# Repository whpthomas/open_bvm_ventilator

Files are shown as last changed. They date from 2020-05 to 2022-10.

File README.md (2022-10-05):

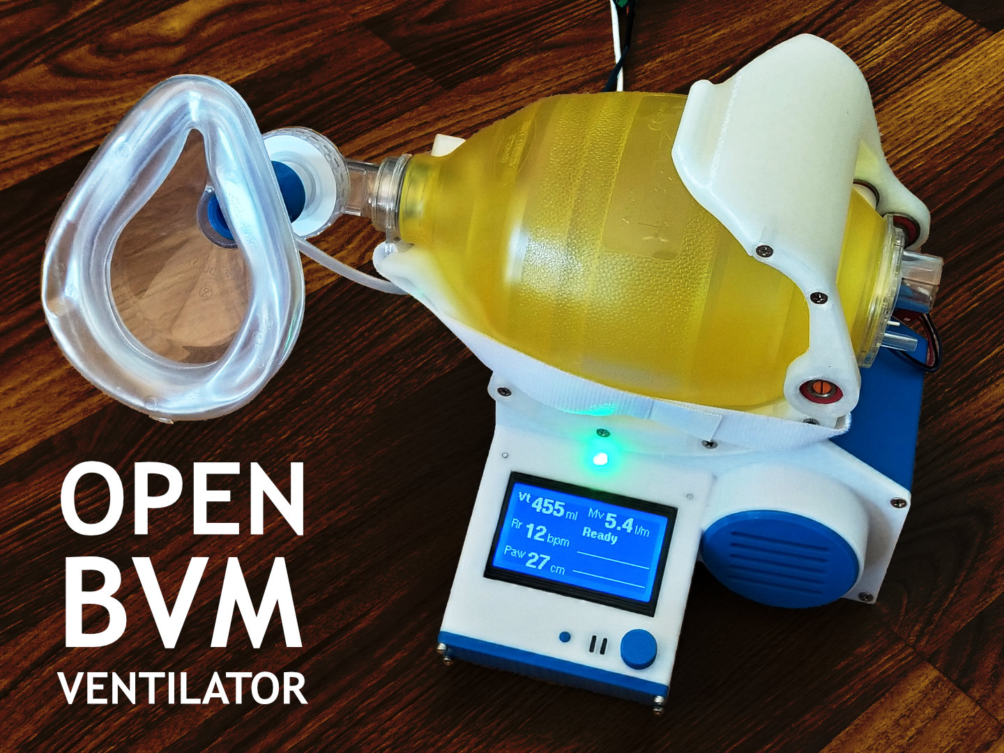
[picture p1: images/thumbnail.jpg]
Open BVM Ventilator


# Open BVM Ventilator project

This is a reference design and test platform for open source non-invasive bag valve mask ventilators. It features 3D printable parts and uses common off-the-shelf hardware and components.

3D Printable files can be found here and on [Thingiverse](https://www.thingiverse.com/thing:4335859).
Fusion 360 CAD files can be found here and on [GrabCAD](https://grabcad.com/library/open-bvm-ventilator-project-1).

## Specification

The Open BVM Ventilator is non-invasive and operates in universal mode (spontaneous pressure triggered ventilation with pressure-limited mandatory ventilation). It has been designed to meet all the applicable requirements outlined in the [Ventilator for COVID-19 use in Australia](spec/ventilator-covid-19-use-australia.pdf) document published on the [Australian Government, Department of Health, Therapeutic Goods Administration](https://www.tga.gov.au/ventilator-covid-19-use-australia) website.

### Assumptions

At the time this design was initiated it was assumed that early non-invasive ventilation with supplementary oxygen is beneficial for treating COVID-19 patients.

In order to meet all the requirements in the above document it is assumed that:

1. Supplementary oxygen will be provided to the bag via an externally regulated source (i.e. an oxygen cylinder or wall outlet).
2. A [HEPA exhalation filter](bom/BOM.md) will be installed between the manifold and mask.
3. A [PEEP regulator](bom/BOM.md) will be installed on the valve output to provide positive end-expiratory pressure.
4. An [extension hose](bom/BOM.md) may be used to connect the mask to the patient. However if used, the extension hose should be connected between the bag and the valve to limit the amount of dead space in the gas exchange.
5. The mask will be strapped to patient in order to provide a hands free airtight seal.

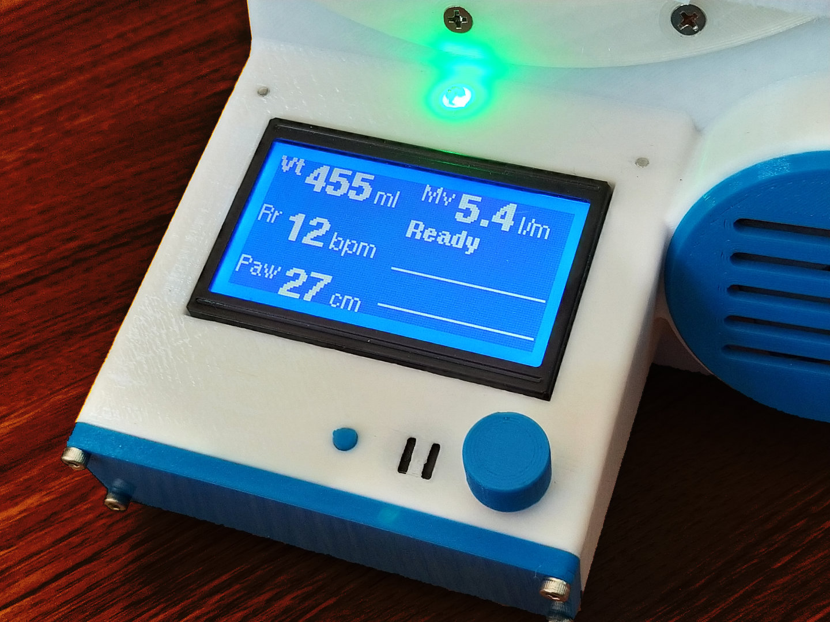
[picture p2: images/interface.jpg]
Open BVM Ventilator Interface


### Capabilities

The current Open BVM Ventilator design has the following capabilities:

* Respiratory air and oxygen is fed through a bag valve mask (Ambu bag) which is an approved medical device for hand resuscitation. The pressure sensor manifold is 3D printed with food grade PLA.
* All controls are adjustable in real time and provide live feedback though mechanical output and the user interface.
* Minute Volume (Mv) and Peak Inspiratory Pressure (Pip) are displayed after each respiratory cycle.
* Pressure-limited mandatory ventilation is controlled via the Respiratory Rate (Rr) and Tidal Volume (Vt).
* Spontaneous ventilation is triggered via negative pressure on the the pressure sensor attached to the manifold (Controls page / Trigger Pressure). 
* Positive end expiratory pressure (PEEP) is provided by a [regulator](bom/BOM.md) attached to the valve output.
* Quick adjustment of Tidal Volume (Vt), Respiratory Rate (Rr) and Plateau Airway Pressure (Paw) is available on the user interface main page.
* Airway pressure safety is set via the maximum pressure limit (Limits page / Pressure / Maximum).
* Pressurised air is not required, therefore the unit can be operated outside of an ICU using only bottled oxygen and a power supply.
* All ventilator controls are accessed via the LCD display, stop button and encoder on the [Reprap Discount Full Graphic Smart Controller](https://reprap.org/wiki/RepRapDiscount_Full_Graphic_Smart_Controller).
* Tidal Volume has been [calibrated and verified](spec/calibration.pdf).
* Both visual and audible alarms are generated and logged on the Events page.
* 12v power can be provided via an AC adapter or external battery.
* All parts can be 3D printed with food safe PLA plastic.

These capabilities have been verified with static tests using a manometer but will require more comprehensive dynamic testing to be considered validated. Some dynamic testing using a water column to simulate pressure and volume has also been undertaken.

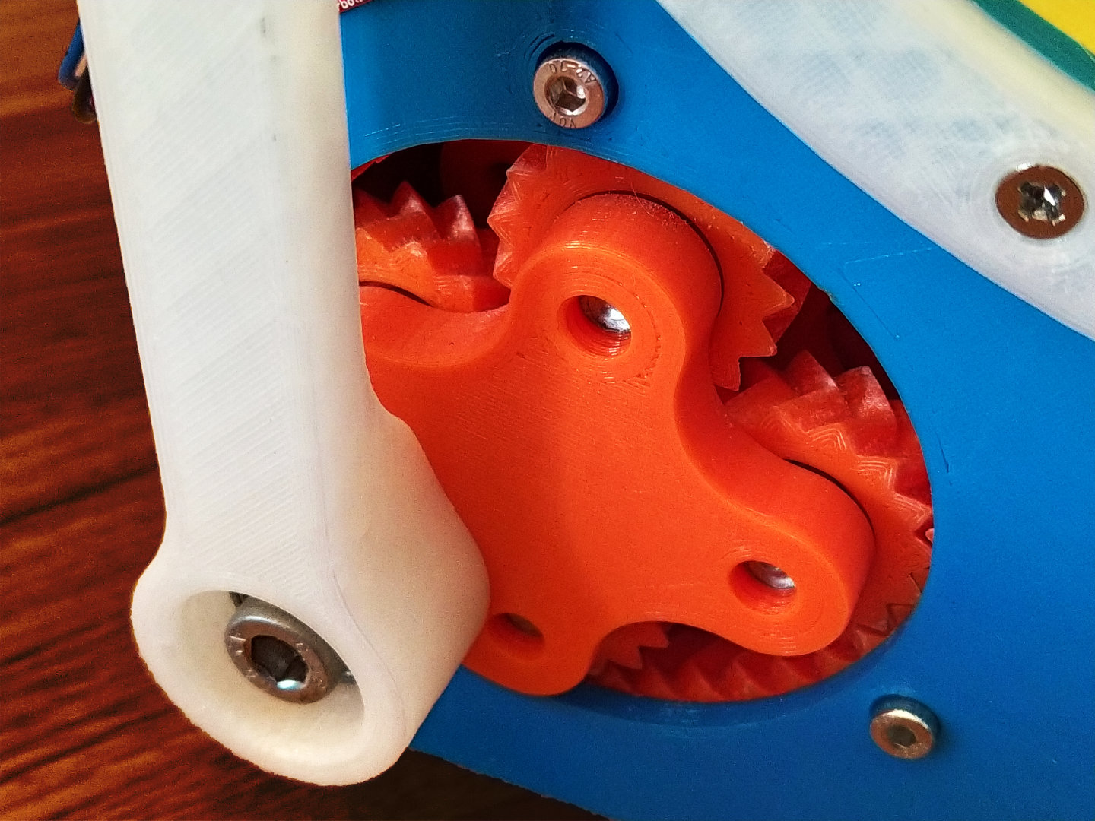
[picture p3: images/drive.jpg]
Open BVM Ventilator Drive


### Outstanding Issues

1. Maximum inspiratory and expiratory flow is limited to 35 l/min by the maximum stepper motor RPM and torque. I will attempt to resolve this by using a TMC2209 driver and by adding a DC Step Up to 24v for the Stepper motor power supply.
2. The current stepper driver is noisy and will to be replaced with a TMC2209 driver. However this will require the addition of a cooling fan.
3. **Time and resources:** when I started this project a critical lack of ventilators was in the news. Now that we have *flattened the curve* - particularly here in Australia - not so much. I self-funded this project and spent weeks working on it. I need to get back to work and earn a living, so unless others want to pitch in and help, I am not sure how much more I can do on my own.

## Hardware

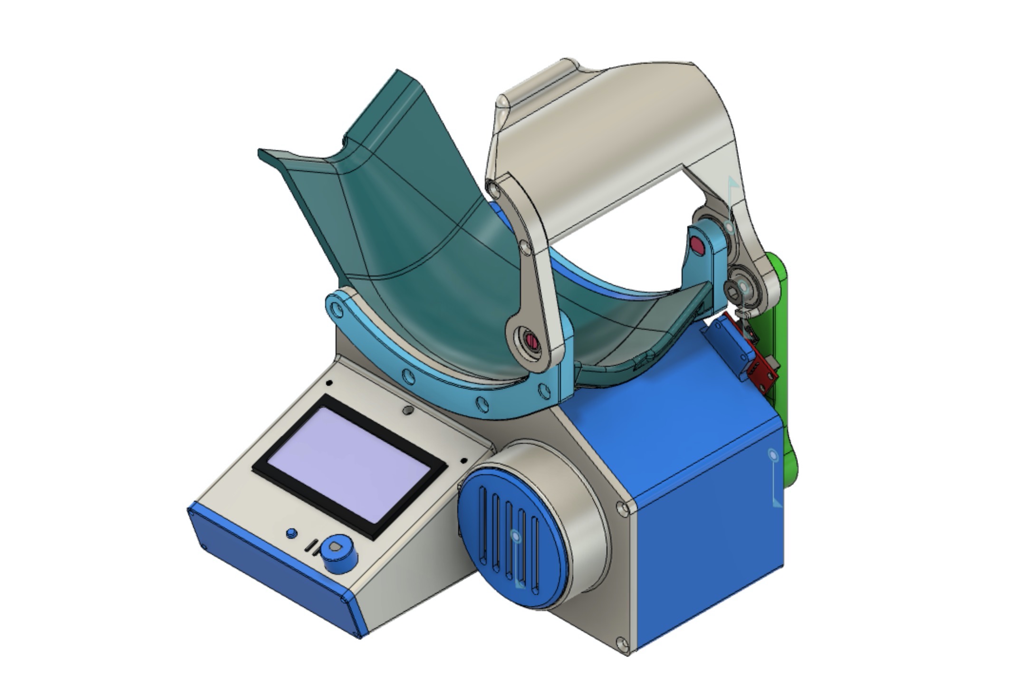
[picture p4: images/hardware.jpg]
Open BVM Ventilator Hardware


The Open BVM Ventilator is comprised of 25 x 3D printed parts and various off-the-shelf hardware, electronic components and fasteners.

A list of all the required hardware, fasteners, electronic components and 3D printed parts can be found in the **[Bill of Materials](bom/BOM.md)**.

## Firmware

The firmware features a real time model view controller architecture with custom stepper speed control that supports linear acceleration with rpm adjustment inside position changes.

The firmware can be downloaded, compiled and uploaded to the Arduino Uno board using the [Arduino IDE](https://www.arduino.cc/). 

The firmware is dependent on the following libraries:

* [BME280I2C](https://github.com/finitespace/BME280)
* [FastIO](https://github.com/whpthomas/FastIO)
* [U8g2lib](https://github.com/olikraus/u8g2)

The factory reset function found on the System Page should be selected the first time the system is run to set all the EEPROM control variables to know values.

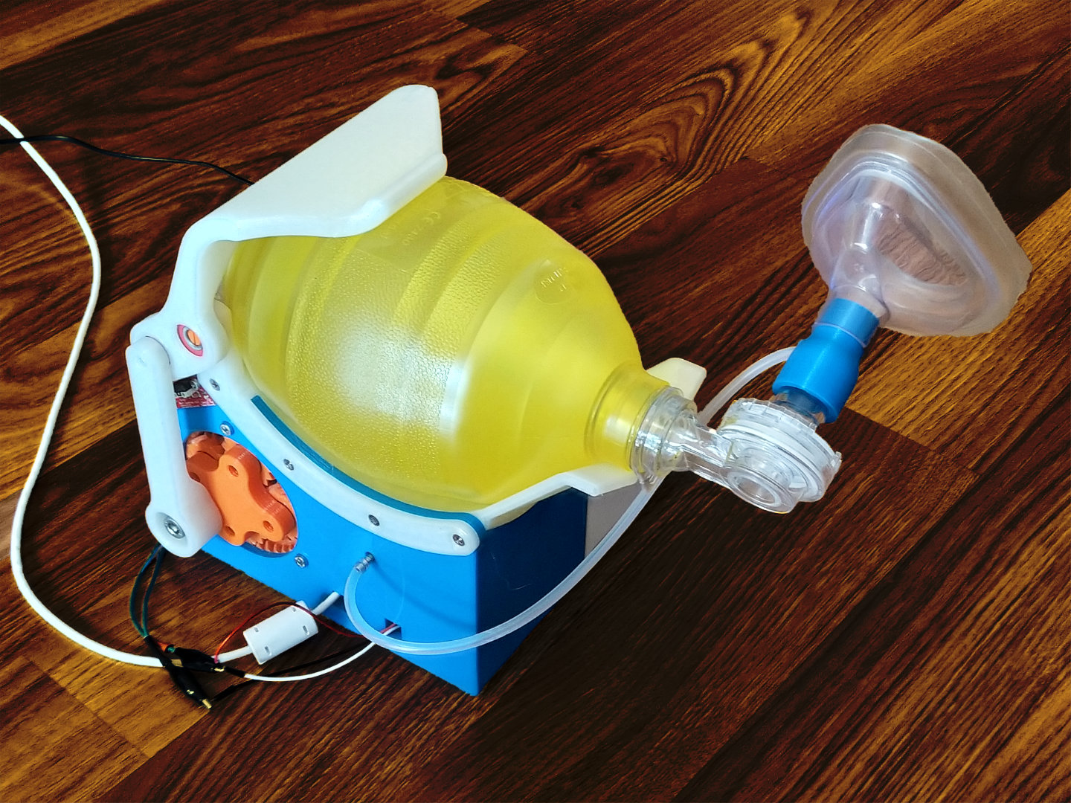
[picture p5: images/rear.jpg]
Open BVM Ventilator Rear


## Electronics

A control shield for the Arduino Uno can be found at [easyeda.com/whpthomas/open-bvm-ventilator-shield](https://easyeda.com/whpthomas/open-bvm-ventilator-shield). The shield has been designed to allow all the electronic components to be easily connected using either Dupont connectors or by directly soldered wires. The circuit supports use of either the TB6560 or A4988 (or compatible) stepstick driver.

Fully assembled boards can be ordered directly from [JLCPCB](https://jlcpcb.com/), [PCBWay](https://www.pcbway.com/) or other suitable PCB prototyping services using the Gerber files, bill of materials and pick and place files found in the [`/pcb`](https://github.com/whpthomas/open_bvm_ventilator/tree/master/pcb) folder.

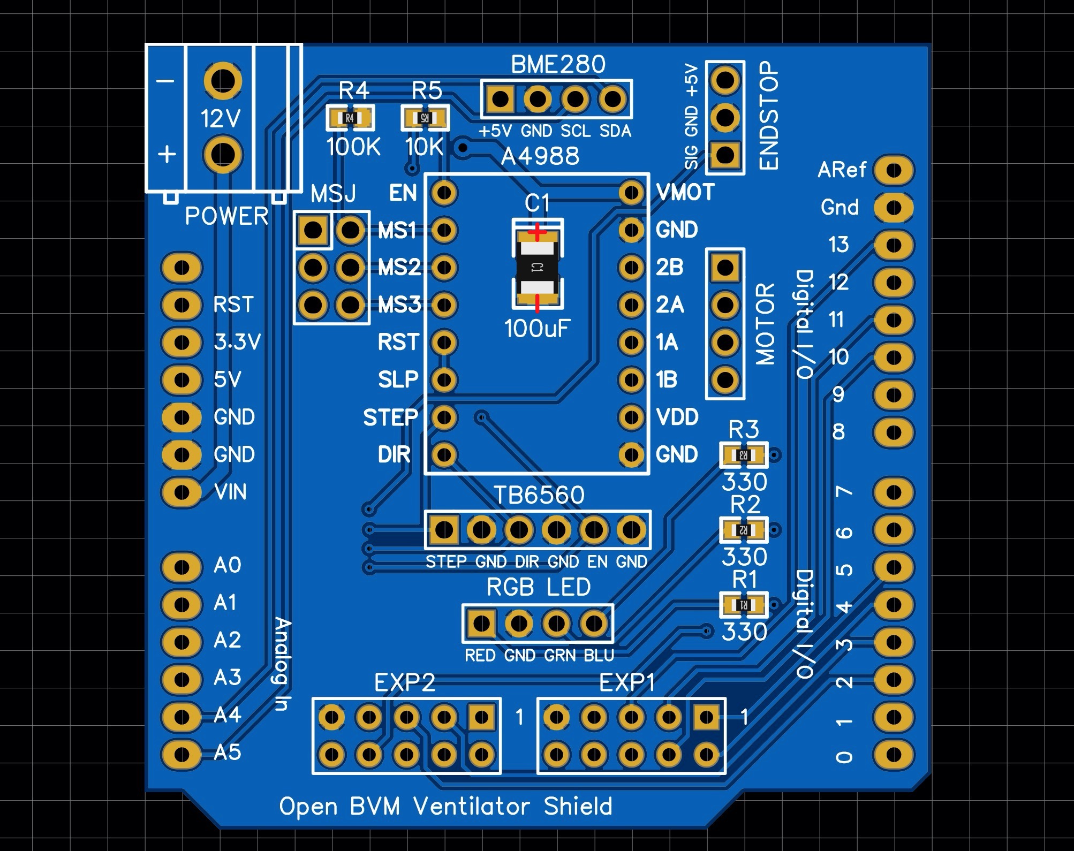
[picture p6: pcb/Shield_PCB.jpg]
Arduino Uno Shield


The following digital pins on the Arduino Uno are used in the [schematic](https://github.com/whpthomas/open_bvm_ventilator/blob/master/pcb/Shield_SCH-v1.pdf):

* **2** Controller Rotary Encoder A (Interrupt 0)
* **3** Controller Rotary Encoder B (Interrupt 1)
* **4** Controller Rotary Encoder Button
* **5** Controller Buzzer
* **6** Controller Stop Button
* **7** LED Red
* **8** LED Green
* **9** LED Blue
* **10** LCD Chip Select (SS)
* **11** LCD Data In (MOSI)
* **13** LCD Clock (SCK)
* **A0** Home Endstop
* **A1** Stepper Driver Step
* **A2** Stepper Driver Direction
* **A3** Stepper Driver Enable
* **A4** BME280 Pressure Sensor IC2 SDA
* **A5** BME280 Pressure Sensor IC2 SCK

#### A4988 Jumper Settings

Jumpers are used on the MSJ header to set the microstep resolution. The default configuration is to place a jumper across MS1 and MS2 for 1/8 microstep resolution.

MS1|MS2|MS3|Microstep Resolution
----|----|----|----
Low|Low|Low|Full step
High|Low|Low|1/2 step
Low|High|Low|1/4 step
High|High|Low|1/8 step
High|High|High|1/16 step

#### TB6560 Switch Configuration

Switches are used on the TB6560 stepper driver to set the current and microstep resolution.

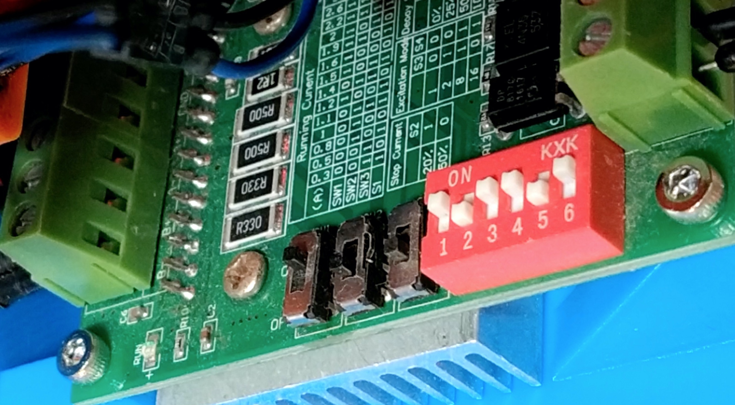
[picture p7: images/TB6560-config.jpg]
TB6560 Configuration


I recommend configuring the TB6560 with the following settings.

Switch|State|Configuration
----|----|----
SW1|ON|1.2A
SW2|OFF|1.2A
SW3|OFF|1.2A
S1|ON|1.2A
S2|OFF|50% Stop Current
S3|ON|1/8 steps
S4|ON|1/8 steps
S5|OFF|50% Delay
S6|ON|50% Delay

----

# TERMS OF USE

Open BVM Ventilator reference designs are intended for educational purposes, ARE NOT CERTIFIED FOR MEDICAL USE, ARE PROVIDED "AS IS" AND "WITH ALL FAULTS". Dr. Henry Thomas DISCLAIMS ALL OTHER WARRANTIES, EXPRESS OR IMPLIED, INCLUDING BUT NOT LIMITED TO, ANY IMPLIED WARRANTIES OF MERCHANTABILITY OR FITNESS FOR A PARTICULAR PURPOSE. Dr. Henry Thomas may make changes to reference design specifications and descriptions at any time, without notice.

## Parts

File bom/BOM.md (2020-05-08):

# Bill of Materials

This is the bill of materials for the [Open BVM Ventilator](https://github.com/whpthomas/open_bvm_ventilator) project. Where possible I have chosen widely available common off-the-shelf (COTS) components. However the machine screws I used are metric which may be harder to source in North America.

## Medical Supplies

Part|Description|Quantity
----|----|----
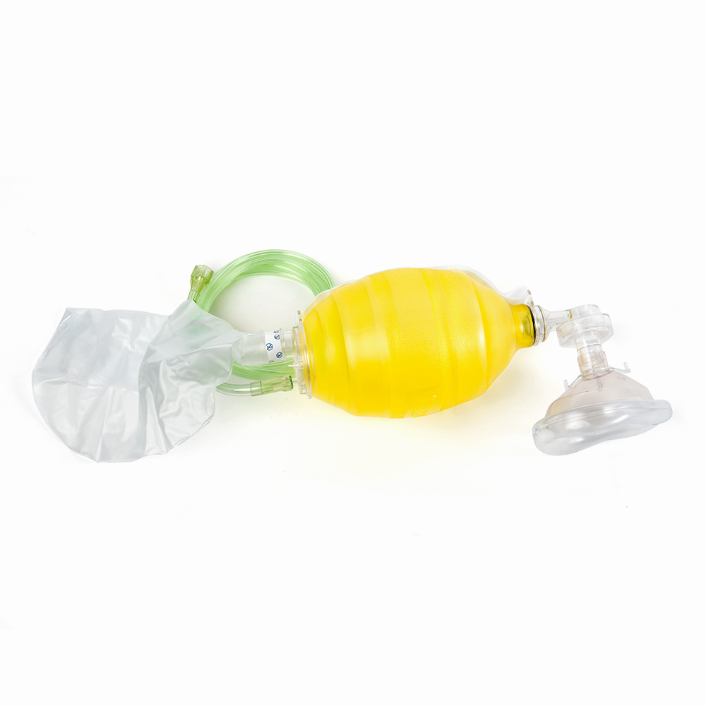
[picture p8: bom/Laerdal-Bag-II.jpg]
Laerdal Bag II
|[Laerdal Bag II](https://www.laerdal.com/au/item/845111), [LSR](https://www.laerdal.com/au/item/87005133), or equivalent adult sized bag valve mask hand  resuscitator (e.g. Ambu Bag).|1
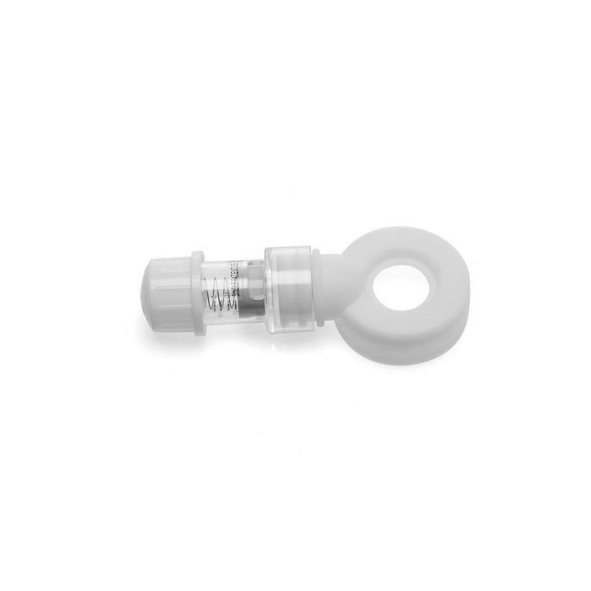
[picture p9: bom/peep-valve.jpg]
PEEP Valve
|[PEEP Valve](https://www.laerdal.com/au/item/845240) (5-20 cm H2O).|1
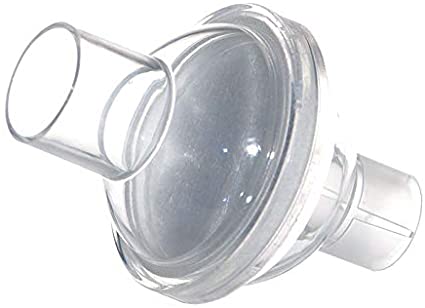
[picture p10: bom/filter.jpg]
HEPA Filter
|HEPA Filter.|1
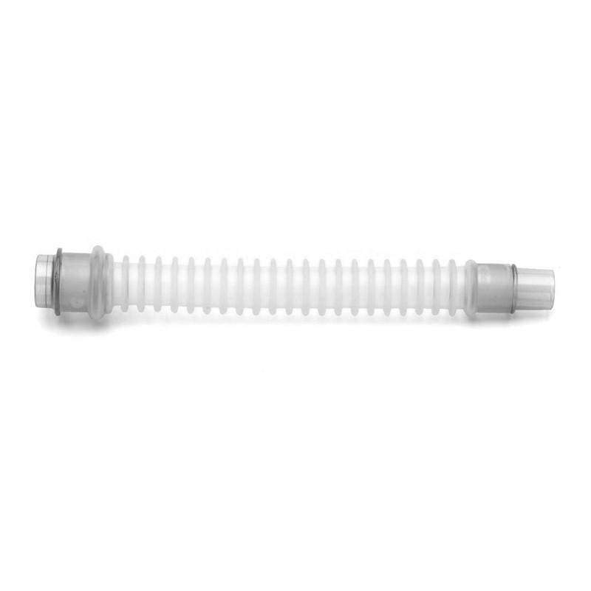
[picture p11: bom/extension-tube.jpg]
Extension Tube
|[Silicone Extension Tube](https://www.laerdal.com/au/item/871000).|1
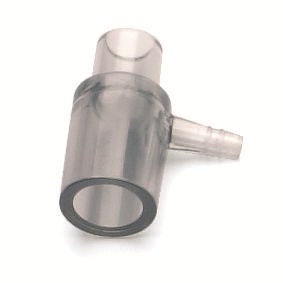
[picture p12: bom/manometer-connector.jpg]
Manometer Connector
|[Manometer connector](https://www.laerdal.com/au/item/850900). This barb requires a 6mm oxygen hose.|Option

## Hardware

Part|Description|Quantity
----|----|----
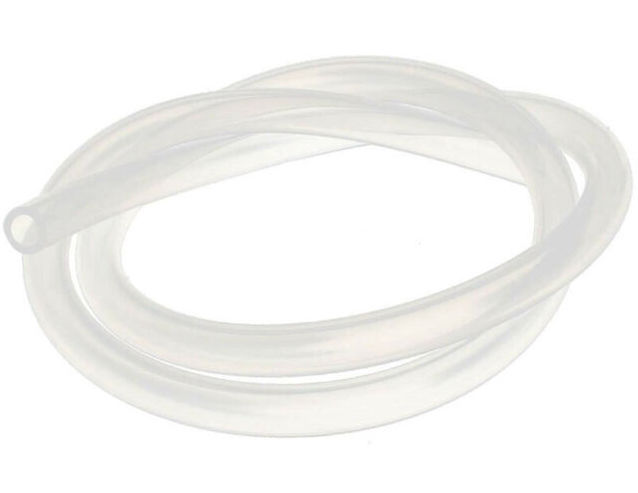
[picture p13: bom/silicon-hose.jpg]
Silicon Hose
|5mm OD x 3mm ID x 250mm L food grade silicon hose.|1
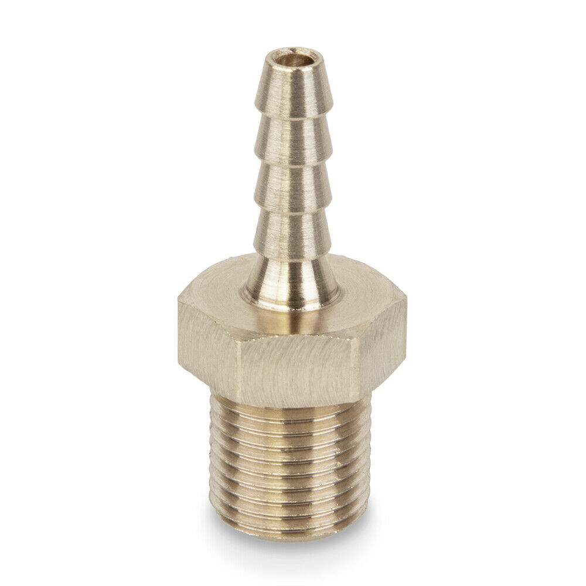
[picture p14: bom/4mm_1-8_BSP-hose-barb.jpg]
Hose Fitting
|1/8" BSP to 4mm barb hose fitting. This barb protrudes from the back of the housing base and is used to connect the manifold hose to the pressure sensor. If you decide to use the optional [manometer connector](https://www.laerdal.com/au/item/850900) a 1/8" BSP to **6mm** barb hose fitting should be used.|1
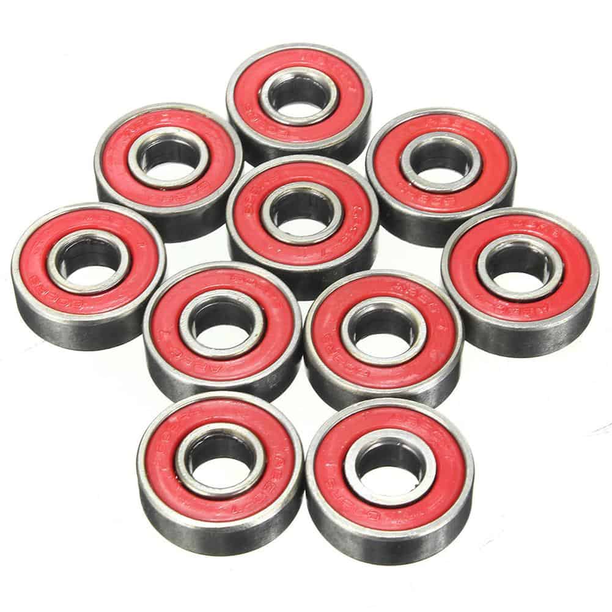
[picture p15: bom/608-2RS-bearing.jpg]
Bearing
|608-2RS 22mm OD x 8mm ID x 7mm W skate bearings.|11
M3x6mm Machine Screws|M3 x 6mm stainless socket head cap screws are used to attach the stepper motor to the ring mount, and the Arduino Uno, stepper driver and endstop circuit boards to the base.|13
M3x12mm Machine Screws|M3 x 12mm stainless socket head cap screws are used to attach the interface front cover to the interface panel.|4
M3x16mm Machine Screws|M3 x 16mm stainless socket head cap screws are used to attach the [Reprap Discount Full Graphic Smart Controller](https://reprap.org/wiki/RepRapDiscount_Full_Graphic_Smart_Controller) to the interface panel.|2
M4x12mm Countersink Screws|M4 x 12mm stainless countersink screws are used to assemble the cradle, hinges and main housing.|13
M4x16mm Machine Screws|M4 x 16mm stainless socket head cap screws are used to assemble the planetary gear module and attache it to the housing.|12
M8x16mm Machine Screws|M8 x 16mm stainless socket head cap screws are used to attach bearings to the planet intermediate carrier to gang 1, bearings the planetary output carrier to gang 2 and bearings to the tie rod between the planetary output and press arm.|10

## Electronic components

Part|Description|Quantity
----|----|----
Arduino Uno|Arduino Uno Rev 3|1
BME280 Sensor Module|BME280 humidity, barometric pressure and temperature sensor module with 3 wire I2C interface.|1
Makerbot endstop|Makerbot 3D printer endstop.|1
Stepper Motor|NEMA17 2 phase stepper motor with 1.8 degree step angle, 60mm motor length, and 1.5A current rating.|1
Power Supply|12 volt 1 amp AC-DC power supply with 5.5mm OD 2.5mm ID center-positive DC plug.|1
RGB LED|Common cathode 5mm RGB LED.|1
Arduino Uno|[Reprap Discount Full Graphic Smart Controller](https://reprap.org/wiki/RepRapDiscount_Full_Graphic_Smart_Controller). This component is a widely available LCD interface controller commonly used on many 3D printers.|1
Stepper Driver| TB6560 stepper driver.|1
Jumper Wires|Bread board jumper wires|20 leads

## 3D printed parts

These parts can be printed in PLA or PETG on a 200mm W x 150mm D x 150mm H bed.

Part|Description|Quantity
----|----|----
Base|`base.stl` This part comprises the main body of the ventilator housing. The circuit boards and planetary drive are mounted inside this enclosure.|1
Bearing Pin|`bearing_pin.stl`These press fitted parts connect the the 608 bearings in the press arm assembly to the left an right hinge plates.|2
Control Knob|`control_knob.stl` This part is press fitted onto the encoder of the [Reprap Discount Full Graphic Smart Controller](https://reprap.org/wiki/RepRapDiscount_Full_Graphic_Smart_Controller)|1
Cradle|`cradle.stl` This part links the housing base and interface panel with the left and right hinge plates.|1
Hex Link|`hex_link.stl` This part connects the Planet Intermediate carrier with the Planetary Gear module 2.|1
Hinge Plate Right|`hinge_plate_l.stl` This part connects the press arm assembly to the the cradle and housing.|1
Hinge Plate Left|`hinge_plate_r.stl` This part connects the press arm assembly to the the cradle and housing.|1
Interface Front Cover|`interface_front_cover.stl` This part attaches to the front interface panel and holds the [Reprap Discount Full Graphic Smart Controller](https://reprap.org/wiki/RepRapDiscount_Full_Graphic_Smart_Controller) in place.|1
Interface Panel|`interface-panel.stl` This part is attached to the front of the base housing.|1
Mask Manifold|`mask_manifold.stl` This part attaches between the mask and valve and connects the opposite end of the 5mm silicon hose with the pressure sensor.|1
Motor Cover|`motor_cover.stl` This part snaps onto the interface panel and covers the rear of the stepper motor.|1
Planet Intermediate|`planet_intermediate.stl` This carrier holds the planetary gang 1 bearings in place and drives gang 2 via the hex link.|1
Planet Output|`planet_output.stl` This carrier holds the planetary gang 2 bearings in place and drives the tie rod.|1
Planetary Gear Module Gang 1|`planetary_gang_1_x-x.stl` This part is the gang 1 print-in-place planetary gear module. There are two versions of this file, one for a steeper motor with a 3.9mm keyway and the other for a 4.5mm keyway.|1
Planetary Gear Module Gang 2|`planetary_gang_2.stl` This part is the gang 2 print-in-place planetary gear module which is driven via the hex link by the intermediate carrier.|1
Press Bracket|`press_bracket.stl` This bracket is attached to opposite side of the press arm.|1
Press Arm|`press-arm.stl` This part is attached via bearings and pins to the hinge plates.|1
Pressure Sensor Base|`pressure_sensor_base.stl` This part encloses the BME280 sensor, that should be sealed with Sikaflex 227 (or equivalent).|1
Pressure Sensor Mount|`pressure_sensor_mount.stl` This part connects the BME280 sensor to the 4mm hose barb and is attached to the base with cyanoacrylate gel glue.|1
Ring Mount|`ring_mount.stl` This part connects the planetary gear module to the stepper motor.|1
Ring Spacer|`ring_spacer.stl` This part connects the planetary gear gang 1 & 2 together.|1
Spacer|`spacer.stl` This part separates the tie rod bearing from the planetary output carrier.|1
Stop Button|`stop-button.stl` This part links the tactile switch on the [Reprap Discount Full Graphic Smart Controller](https://reprap.org/wiki/RepRapDiscount_Full_Graphic_Smart_Controller) with the interface panel.|1
Tie Rod|`3dp-tie-rod.stl` This part links the planetary output carrier with the press arm.|1

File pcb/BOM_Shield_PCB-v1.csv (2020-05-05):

ID | Name | Designator | Footprint | Quantity | Manufacturer Part | Manufacturer | Supplier | Supplier Part | LCSC Assembly
1 | 100K | R4 | R0603 | 1 | 0603WAF1003T5E | UniOhm | LCSC | C25803 | Yes
2 | 10K | R5 | R0603 | 1 | 0603WAF1002T5E | UniOhm | LCSC | C25804 | Yes
3 | 100uF | C1 | CAP-SMD_L7.3-W4.3-R-RD | 1 | TAJE107M025RNJ | AVX | LCSC | C7230 | Yes
4 | 330 | R3,R1,R2 | R0603 | 3 | 0603WAF3300T5E | UniOhm | LCSC | C23138 | Yes

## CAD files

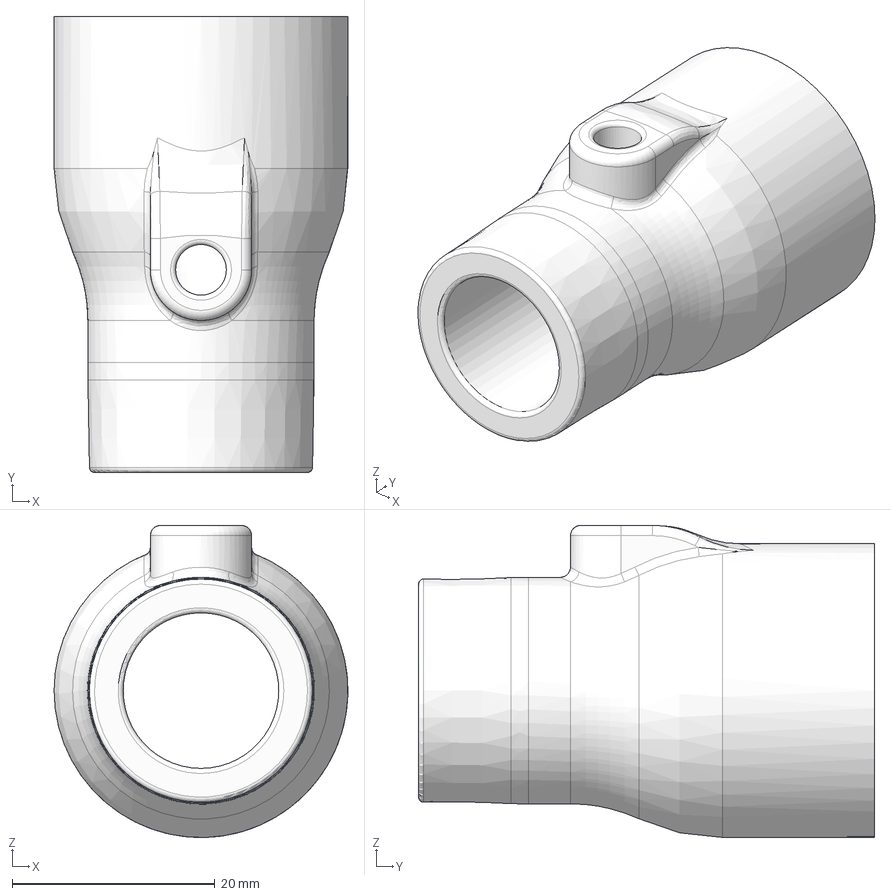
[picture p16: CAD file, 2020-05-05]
cad/Mask Manifold v5.step
29.0 x 45.0 x 30.8 mm

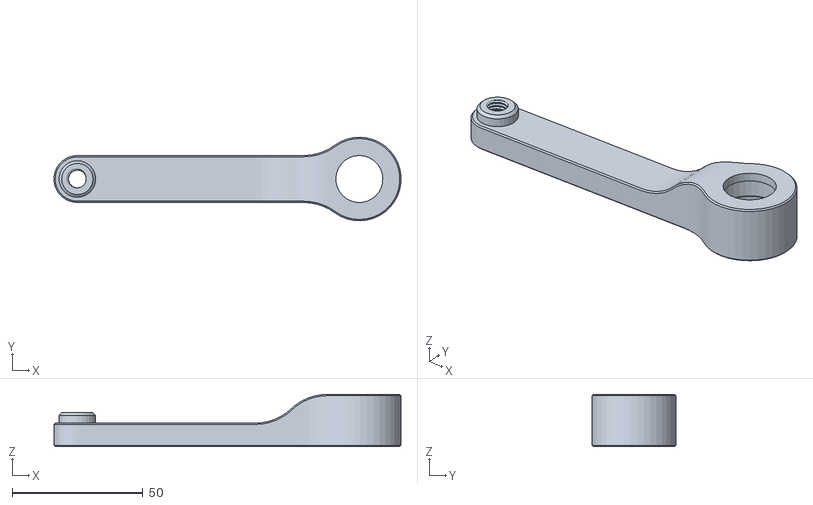
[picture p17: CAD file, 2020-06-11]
stl/tie_rod.stl
132.9 x 32.0 x 20.0

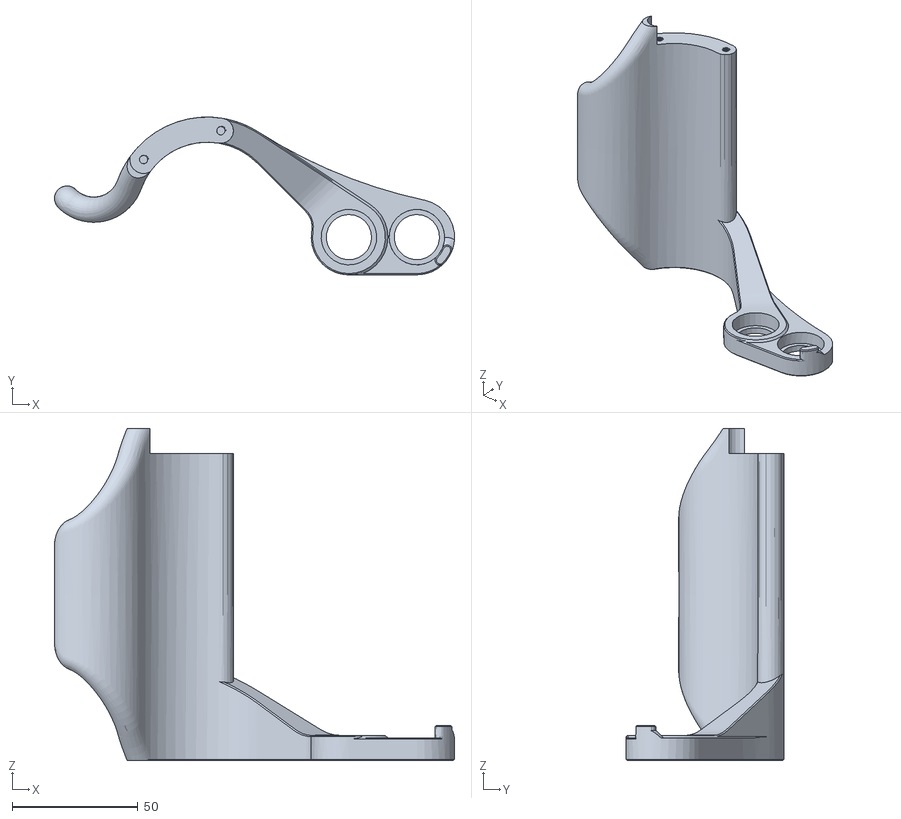
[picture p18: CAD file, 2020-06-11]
stl/press_arm.stl
159.0 x 62.7 x 132.0

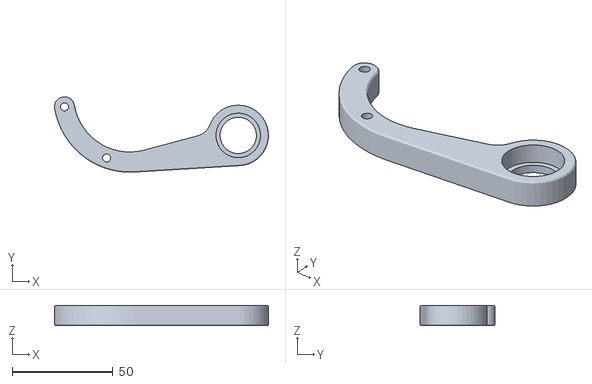
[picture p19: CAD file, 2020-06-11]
stl/press_bracket.stl
106.1 x 37.3 x 10.0

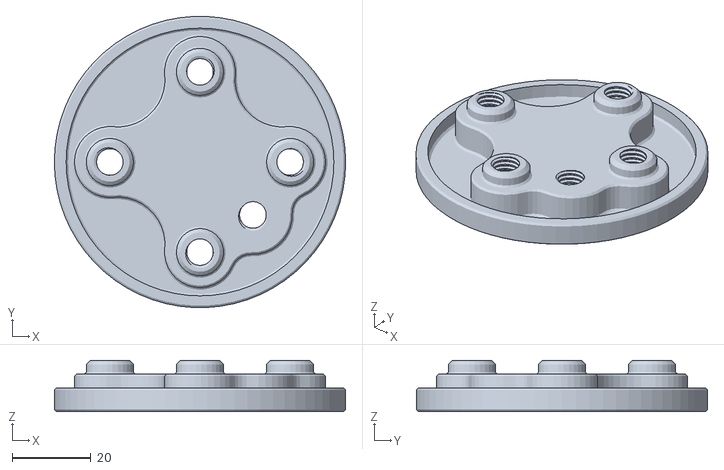
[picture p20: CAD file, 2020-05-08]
stl/planet_output.stl
74.0 x 73.9 x 13.0

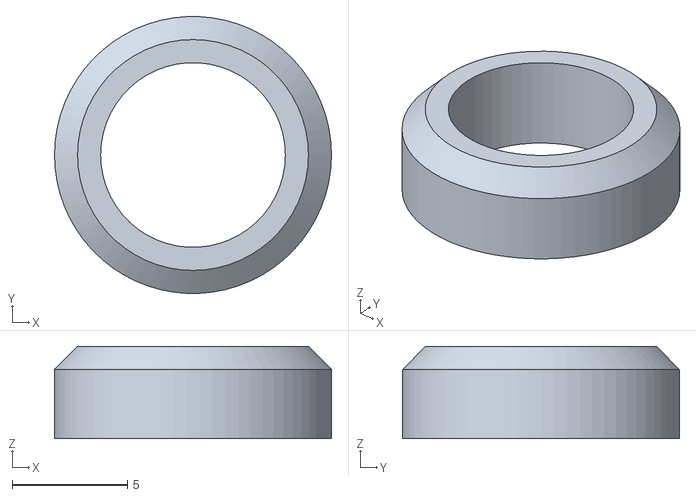
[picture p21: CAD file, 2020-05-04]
stl/spacer.stl
12.0 x 12.0 x 4.00

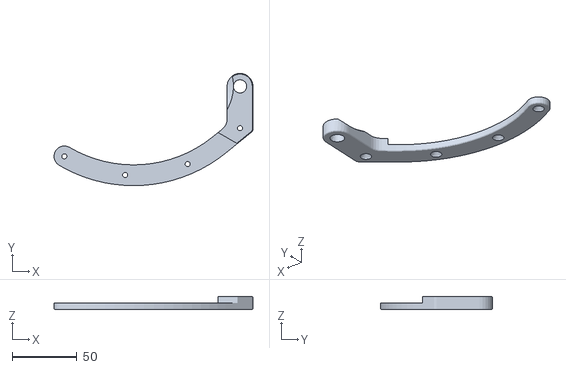
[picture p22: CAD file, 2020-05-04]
stl/hinge_plate_l.stl
153.5 x 86.6 x 10.00

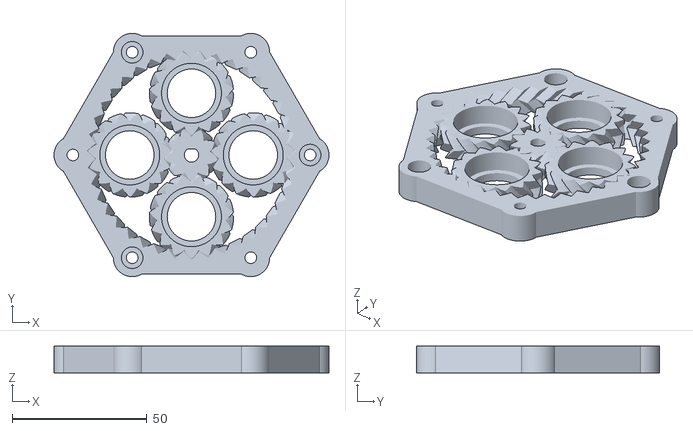
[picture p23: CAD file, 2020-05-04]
stl/planetary_gang_1_4-5.stl
102.0 x 90.2 x 10.0

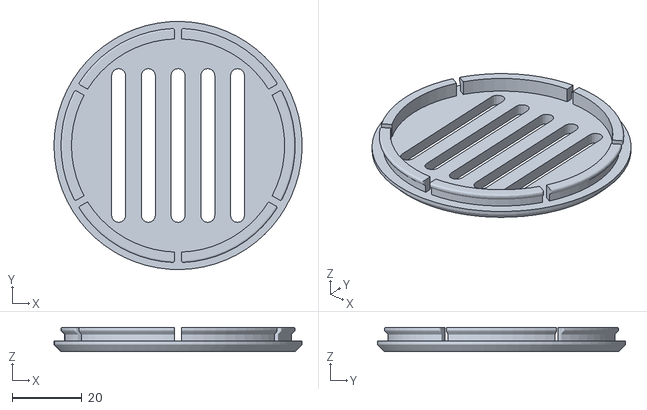
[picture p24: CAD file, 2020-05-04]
stl/motor_cover.stl
71.0 x 71.0 x 7.00

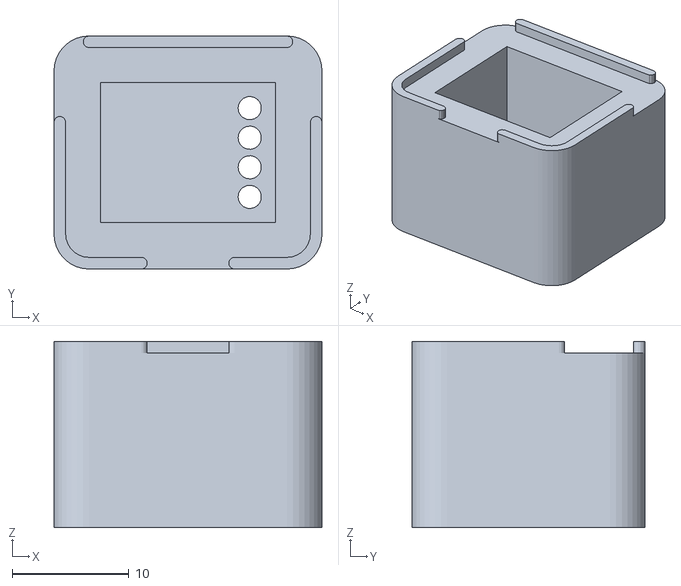
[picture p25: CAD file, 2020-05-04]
stl/pressure_sensor_base.stl
23.0 x 20.0 x 16.0

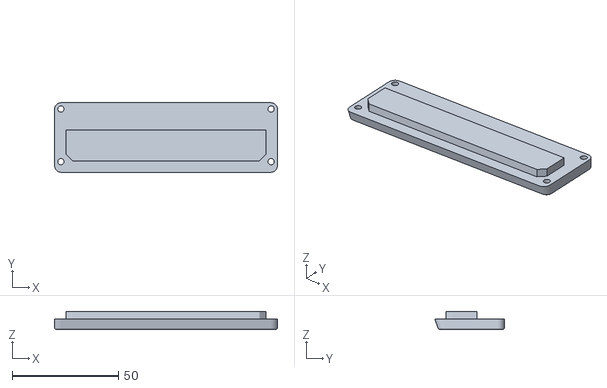
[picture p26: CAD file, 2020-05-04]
stl/interface_front_cover.stl
105.0 x 32.8 x 8.50

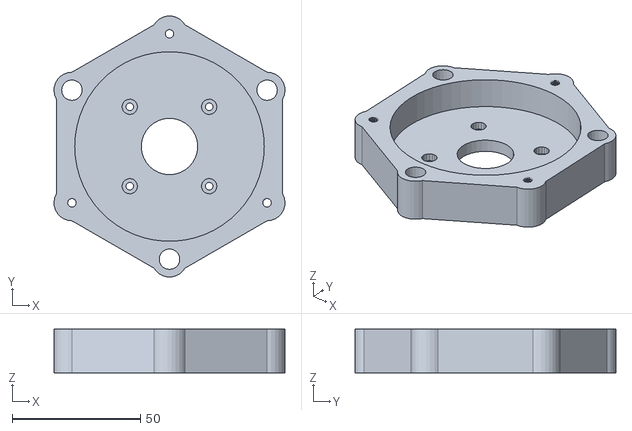
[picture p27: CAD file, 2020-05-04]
stl/ring_mount.stl
90.2 x 101.9 x 17.0

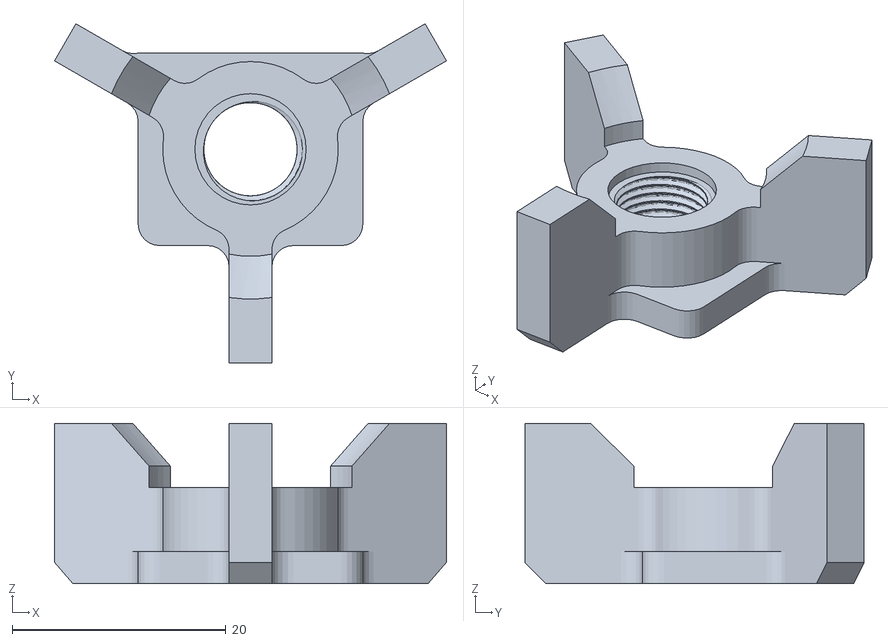
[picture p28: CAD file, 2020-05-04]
stl/pressure_sensor_mount.stl
36.6 x 31.7 x 15.0

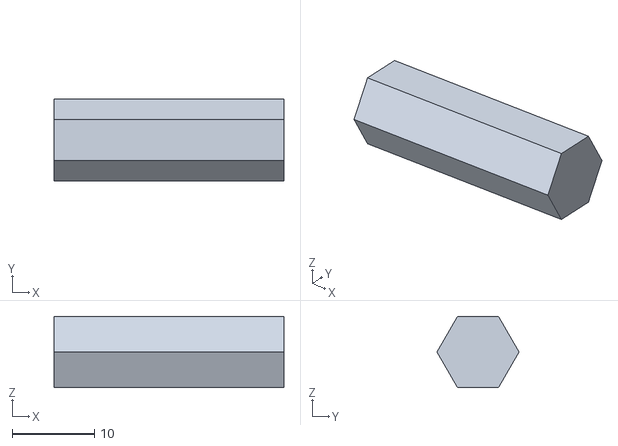
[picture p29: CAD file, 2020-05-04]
stl/hex_link.stl
28.0 x 10.0 x 8.66

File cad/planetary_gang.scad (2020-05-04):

//  Open BVM Ventilator - planetary gear drive train
//
//  Created by WHPThomas <me(at)henri(dot)net> on 20/02/20.
//  Copyright (c) 2020 WHPThomas
//
//  This program is free software: you can redistribute it and/or modify
//  it under the terms of the GNU General Public License as published by
//  the Free Software Foundation, either version 3 of the License, or
//  (at your option) any later version.
//
//  This program is distributed in the hope that it will be useful,
//  but WITHOUT ANY WARRANTY; without even the implied warranty of
//  MERCHANTABILITY or FITNESS FOR A PARTICULAR PURPOSE.  See the
//  GNU General Public License for more details.
//
//  You should have received a copy of the GNU General Public License
//  along with this program.  If not, see <https://www.gnu.org/licenses/>.

// IF YOU ARE HAVING TROUBLE PRINTING THIS PART START BY CHANGING THE
// FILIMENT DIAMETER OR FLOW RATE IN YOUR 3D PRINTER SLICER SOFTWARE.

// planetary gear module [enter 1 or 2] axle or hex keyed drive
gang=1;

// gear mesh clearance
tolerance=0.125;

// center drive shaft diameter clearance
center_clearance=0.15;

// bearing clearance
bearing_clearance=0.1;

// stepper motor drive shaft diameter
drive_shaft_diameter=5.0;

// stepper motor drive shaft edge to flat key surface
drive_shaft_key=3.9; // 3.9 or 4.5

D=86; // diameter of ring
T=10; // thickness
number_of_planets=4;
number_of_teeth_on_planets=15;
approximate_number_of_teeth_on_sun=9;
P=45; //[30:60] pressure angle
nTwist=0.75; // number of teeth to twist across
planet_bearing_diameter=22;
planet_hole_diameter=planet_bearing_diameter-4;
ring_radius=round(D/2+8); // outer hexagon
mount_radius=round(D/2+1); // bolt center radius
mount_hole_diameter=4;
mount_cap_diameter=8; // cap screw head radius
mount_boss_radius=7;
DR=0.5*1;// maximum depth ratio of teeth
m=round(number_of_planets);
np=round(number_of_teeth_on_planets);
ns1=approximate_number_of_teeth_on_sun;
k1=round(2/m*(ns1+np));
k= k1*m%2!=0 ? k1+1 : k1;
ns=k*m/2-np;
nr=ns+2*np;
pitchD=0.9*D/(1+min(PI/(2*nr*tan(P)),PI*DR/nr));
pitch=pitchD*PI/nr;
helix_angle=atan(2*nTwist*pitch/T);
planet_radius=pitchD/2*(ns+np)/nr; // 21.92
phi=$t*360/m;
ko=drive_shaft_key-(drive_shaft_diameter/2)+1;

echo(str("Teeth on planets: " , np));
echo(str("Teeth on sun: " , ns));
echo(str("Pitch: " , pitch));
echo(str("Helix angle: " , helix_angle));
echo(str("Planet diameter: " , planet_radius * 2));
echo(str("Ring diameter: " , ring_radius * 2));
echo(str("Bolt center diameter: " , mount_radius * 2));

translate([0,0,T/2]){
    // ring
	difference(){
        union() {
            // outer ring (gusset)
            cylinder(r=ring_radius,h=T,center=true,$fn=6);
           // boss
           for(i=[0:5])
                rotate([0,0,i*60])
                    translate([mount_radius,0,0])
                        cylinder(r=mount_boss_radius,h=T,center=true,$fn=100);
        }
        union() {
            herringbone(nr,pitch,P,DR,-tolerance,helix_angle,T+0.2);
            // hole
            for(i=[0,2,4])
                rotate([0,0,i*60])
                    translate([mount_radius,0,0]) {
                        mirror([0,0,1])
                            cylinder(r=(mount_hole_diameter/2)+center_clearance,h=T+1,center=false,$fn=100);
                            cylinder(r=mount_cap_diameter/2,h=T+1,center=false,$fn=100);
                    }
            for(i=[1,3,5])
                rotate([0,0,i*60])
                    translate([mount_radius,0,0]) {
                            cylinder(r=(mount_hole_diameter/2)+center_clearance,h=T+1,center=false,$fn=100);
                        mirror([0,0,1])
                            cylinder(r=mount_cap_diameter/2,h=T+1,center=false,$fn=100);
                    }
        }
	}
    // sun
    difference() {
        union() {
            rotate([0,0,(np+1)*180/ns+phi*(ns+np)*2/ns])
                difference(){
                    // gear
                    mirror([0,1,0])
                        herringbone(ns,pitch,P,DR,tolerance,helix_angle,T);
                    // hole
                    if(gang==1) 
                        cylinder(r=(drive_shaft_diameter/2)+center_clearance,h=T+1,center=true,$fn=100);
                    else
                        cylinder(r=5+center_clearance,h=T+1,center=true,$fn=6);                    
                }
            // key way
            if(gang==1)
                translate([0,ko+center_clearance,0])
                    cube([6,2,T], true);
        }
    }
    // planets
	for(i=[1:m])
        rotate([0,0,i*360/m+phi])
            translate([planet_radius,0,0])
                rotate([0,0,i*ns/m*360/np-phi*(ns+np)/np-phi])
                    difference(){
                        // gear
                        herringbone(np,pitch,P,DR,tolerance,helix_angle,T);
                        union() {
                            // hole
                            cylinder(r=planet_hole_diameter/2,h=T+1,center=true,$fn=100);
                            // bearing housing
                            translate([0,0,-2]) {
                                cylinder(r=(planet_bearing_diameter/2)+bearing_clearance,h=T+1,center=false,$fn=100);
                            }
                        }
                    }
}

module rack(
	number_of_teeth=15,
	circular_pitch=10,
	pressure_angle=28,
	helix_angle=0,
	clearance=0,
	gear_thickness=5,
	flat=false){
addendum=circular_pitch/(4*tan(pressure_angle));

flat_extrude(h=gear_thickness,flat=flat)translate([0,-clearance*cos(pressure_angle)/2])
	union(){
		translate([0,-0.5-addendum])square([number_of_teeth*circular_pitch,1],center=true);
		for(i=[1:number_of_teeth])
			translate([circular_pitch*(i-number_of_teeth/2-0.5),0])
			polygon(points=[[-circular_pitch/2,-addendum],[circular_pitch/2,-addendum],[0,addendum]]);
	}
}

module herringbone(
	number_of_teeth=15,
	circular_pitch=10,
	pressure_angle=28,
	depth_ratio=1,
	clearance=0,
	helix_angle=0,
	gear_thickness=5){
union(){
	gear(number_of_teeth,
		circular_pitch,
		pressure_angle,
		depth_ratio,
		clearance,
		helix_angle,
		gear_thickness/2);
	mirror([0,0,1])
		gear(number_of_teeth,
			circular_pitch,
			pressure_angle,
			depth_ratio,
			clearance,
			helix_angle,
			gear_thickness/2);
}}

module gear (
	number_of_teeth=15,
	circular_pitch=10,
	pressure_angle=28,
	depth_ratio=1,
	clearance=0,
	helix_angle=0,
	gear_thickness=5,
	flat=false){
pitch_radius = number_of_teeth*circular_pitch/(2*PI);
twist=tan(helix_angle)*gear_thickness/pitch_radius*180/PI;

flat_extrude(h=gear_thickness,twist=twist,flat=flat)
	gear2D (
		number_of_teeth,
		circular_pitch,
		pressure_angle,
		depth_ratio,
		clearance);
}

module flat_extrude(h,twist,flat){
	if(flat==false)
		linear_extrude(height=h,twist=twist,slices=twist/6)children(0);
	else
		children(0);
}

module gear2D (
	number_of_teeth,
	circular_pitch,
	pressure_angle,
	depth_ratio,
	clearance){
pitch_radius = number_of_teeth*circular_pitch/(2*PI);
base_radius = pitch_radius*cos(pressure_angle);
depth=circular_pitch/(2*tan(pressure_angle));
outer_radius = clearance<0 ? pitch_radius+depth/2-clearance : pitch_radius+depth/2;
root_radius1 = pitch_radius-depth/2-clearance/2;
root_radius = (clearance<0 && root_radius1<base_radius) ? base_radius : root_radius1;
backlash_angle = clearance/(pitch_radius*cos(pressure_angle)) * 180 / PI;
half_thick_angle = 90/number_of_teeth - backlash_angle/2;
pitch_point = involute (base_radius, involute_intersect_angle (base_radius, pitch_radius));
pitch_angle = atan2 (pitch_point[1], pitch_point[0]);
min_radius = max (base_radius,root_radius);

intersection(){
	rotate(90/number_of_teeth)
		circle($fn=number_of_teeth*3,r=pitch_radius+depth_ratio*circular_pitch/2-clearance/2);
	union(){
		rotate(90/number_of_teeth)
			circle($fn=number_of_teeth*2,r=max(root_radius,pitch_radius-depth_ratio*circular_pitch/2-clearance/2));
		for (i = [1:number_of_teeth])rotate(i*360/number_of_teeth){
			halftooth (
				pitch_angle,
				base_radius,
				min_radius,
				outer_radius,
				half_thick_angle);		
			mirror([0,1])halftooth (
				pitch_angle,
				base_radius,
				min_radius,
				outer_radius,
				half_thick_angle);
		}
	}
}}

module halftooth (
	pitch_angle,
	base_radius,
	min_radius,
	outer_radius,
	half_thick_angle){
index=[0,1,2,3,4,5];
start_angle = max(involute_intersect_angle (base_radius, min_radius)-5,0);
stop_angle = involute_intersect_angle (base_radius, outer_radius);
angle=index*(stop_angle-start_angle)/index[len(index)-1];
p=[[0,0],
	involute(base_radius,angle[0]+start_angle),
	involute(base_radius,angle[1]+start_angle),
	involute(base_radius,angle[2]+start_angle),
	involute(base_radius,angle[3]+start_angle),
	involute(base_radius,angle[4]+start_angle),
	involute(base_radius,angle[5]+start_angle)];

difference(){
	rotate(-pitch_angle-half_thick_angle)polygon(points=p);
	square(2*outer_radius);
}}

// Mathematical Functions
//===============
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

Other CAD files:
stl/planetary_gang_2.stl
stl/mask_manifold.stl
stl/hinge_plate_r.stl
stl/stop_button.stl
cad/Mask Manifold v5.f3d
cad/Mask Manifold v5.iges
cad/Planetary Gear Module v11.f3z
stl/base.stl
stl/bearing_pin.stl
stl/control_knob.stl
stl/cradle.stl
stl/interface_panel.stl
stl/planet_intermediate.stl
stl/planetary_gang_1_3-9.stl
stl/ring_spacer.stl

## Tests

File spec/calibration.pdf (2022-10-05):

### Sensor Calibration Data

| Actual | Delta | toFn | fromFn
600 | 650 | -50 | 650 | 600
550 | 550 | 0 | 550 | 550
500 | 500 | 0 | 450 | 500
450 | 350 | 100 | 350 | 450
400 | 250 | 150 | 250 | 400
350 | 150 | 200 | 150 | 350
300 | 100 | 200 | 50 | 300
250 | 50 | 200 | -50 | 250
200 | 0 | 200 | -150 | 200

-175

0

175

350

525

700

600 | 550 | 500 | 450 | 400 | 350
Actual | Delta | toFn | fromFn

1

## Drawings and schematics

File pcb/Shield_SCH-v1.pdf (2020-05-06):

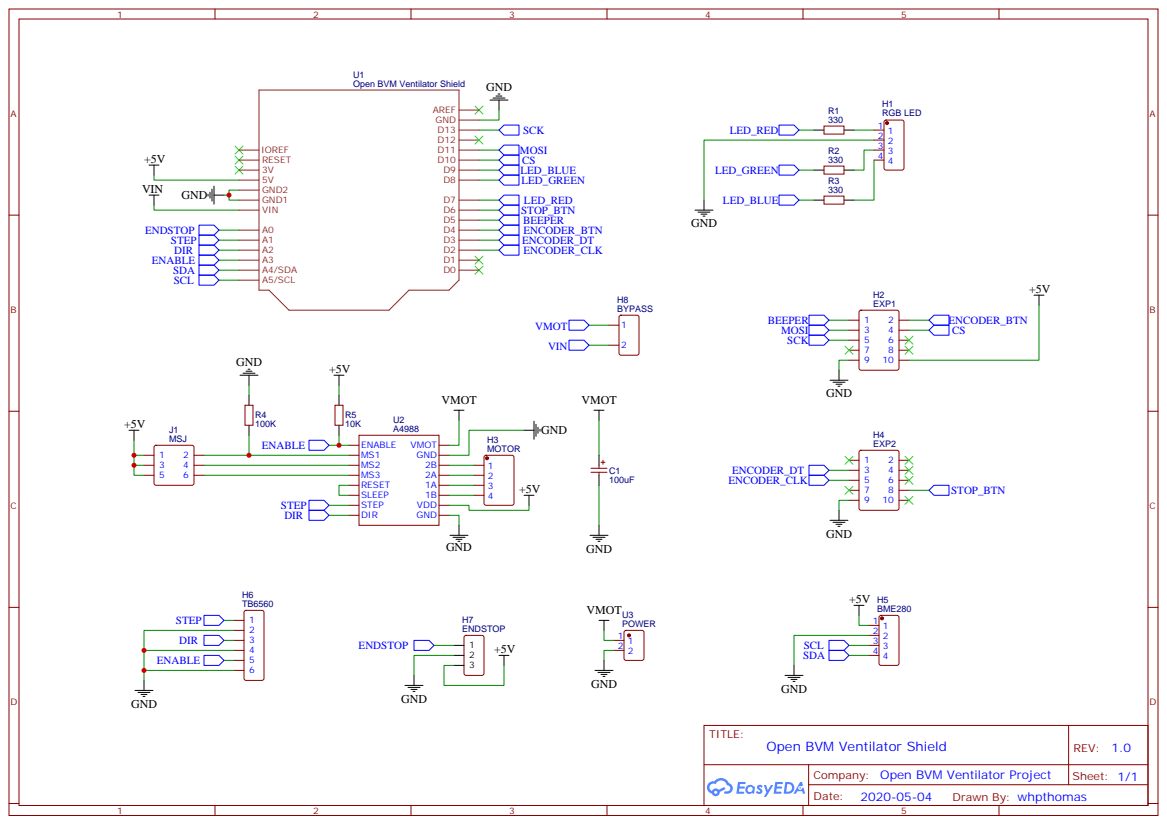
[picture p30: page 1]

Open BVM Ventilator Shield

Company: Open BVM Ventilator Project

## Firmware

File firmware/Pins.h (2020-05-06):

//  Open BVM Ventilator - Arduino UNO/Nano pin assignment
//
//  Created by WHPThomas <me(at)henri(dot)net> on 20/02/20.
//  Copyright (c) 2020 WHPThomas
//
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
#pragma once

#define ROTARY_CLK_PIN      2 // *White
#define ROTARY_DT_PIN       3 // *Grey
#define ROTARY_BUTTON_PIN   4 // Orange

#define BEEPER_PIN          5 // Yellow
#define STOP_BUTTON_PIN     6 // Black

#define RED_PIN             7 // Red
#define GREEN_PIN           8 // Green
#define BLUE_PIN            9 // Blue

#define CS_PIN              10 // Green
#define MOSI_PIN            11 // Blue
#define SCK_PIN             13 // Purple

#define HOME_ENDSTOP_PIN    14 // Blue

#define STEP_PIN            15 // Yellow
#define DIR_PIN             16 // Blue
#define ENABLE_PIN          17 // Green

//#define SDA_PIN             18
//#define SCL_PIN             19

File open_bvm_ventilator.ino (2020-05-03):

//  Open BVM Ventilator
//
//  Created by WHPThomas <me(at)henri(dot)net> on 20/02/20.
//  Copyright (c) 2020 WHPThomas
//
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
#include <Arduino.h>
#include <EEPROM.h>
#include <FastIO.h>
#include <BME280I2C.h>
#include <Wire.h>
#include <avr/wdt.h>

#include "options.h"
#include "Pins.h"
#include "ButtonDebouncer.h"
#include "Control.h"
#include "Draw.h"
#include "Encoder.h"
#include "StepperTimer.h"
#include "StepperSpeedControl.h"

ButtonDebouncer rotaryButton;
ButtonDebouncer stopButton;
ButtonDebouncer homeEndstop;

BME280I2C::Settings settings(
   BME280::OSR_X2,
   BME280::OSR_X1,
   BME280::OSR_X4,
   BME280::Mode_Forced,
   BME280::StandbyTime_500us,
   BME280::Filter_2,
   BME280::SpiEnable_False,
   BME280I2C::I2CAddr_0x76
);

BME280I2C bme(settings);

void select_home_page();
int read_pressure();
void update_pressure();
void adjust_rpm();

void setup() {
  IF_DEBUG( debug.begin(115200); )
  stepper_setup();
  timer1_setup();
  ctrl_setup();
  draw_setup();  
  encoder_setup();

  Wire.begin();
  if(!bme.begin()) {
    Serial.println("Could not find BME280I2C sensor!");
    delay(1000);    
  }
  delay(500);
  live.basePressure = live.zeroPressure = read_pressure();

  IF_DEBUG( debug.println("Started"); )
  fastPinMode(ROTARY_BUTTON_PIN, INPUT_PULLUP);
  fastPinMode(STOP_BUTTON_PIN, INPUT_PULLUP);
  fastPinMode(HOME_ENDSTOP_PIN, INPUT_PULLUP);
  phase = HOME_PHASE;
}

void loop()
{
  unsigned long now = millis();
  static unsigned long redrawTimer;
  static unsigned long inspiratoryTimer;
  static unsigned long breathCycleTimer;
  static unsigned long lastBreathCycle;
  
  /* ROTARY ENCODER BEHAVIOR
   * If value level, change the selection input value within range
   * If menu level, change the selection on the current page
   */

  if(encoder.dir) {
     //IF_DEBUG( debug.println(encoder.dir > 0 ? "clockwise" : "counter clockwise"); )
    switch(level) {
      default: // encoder changes control value 
        switch(selection) {
          /* HOME_PAGE */
          case TIDAL_VOLUME:
            ctrl_tidal_volume(clamp_input_value(ctrl.tidalVolume, 5, encoder.dir, limit.minimum.volume, limit.maximum.volume));
            break;
          case RESPIRATORY_RATE:
            ctrl_respiratory_rate(clamp_input_value(ctrl.respiratoryRate, 1, encoder.dir, 12, 20));
            break;
          case PLATEAU_AIRWAY_PRESSURE:
            ctrl_plateau_airway_pressure(clamp_input_value(ctrl.plateauAirwayPressure, 10, encoder.dir, limit.minimum.pressure, limit.maximum.pressure));
            break;

          /* CONTROLS_PAGE */
          case RESPIRATORY_RATIO:
            ctrl_respiratory_ratio(clamp_input_value(ctrl.respiratoryRatio, 1, encoder.dir, 1, 5));
            break;
          case TRIGGER_PRESSURE:
            ctrl_pressure_trigger(clamp_input_value(ctrl.triggerPressure, 1, encoder.dir, 0, 50));
            break;
          case INSPIRATORY_FLOW:
            ctrl_inspiratory_flow(clamp_input_value(ctrl.inspiratoryFlow, 1, encoder.dir, 10, 60));
            break;
          case EXPIRATORY_FLOW:
            ctrl_expiratory_flow(clamp_input_value(ctrl.expiratoryFlow, 1, encoder.dir, 10, 60));
            break;

          /* SETUP PAGE */
          case START_STOP_VENTILATION:
            break;
          case PRESSURE_TEST:
            break;

          /* LIMITS_PAGE */
          case PRESSURE_LIMIT:
            if(level == OTHER_VALUE_LEVEL) {
              limit_minimum_pressure(clamp_input_value(limit.minimum.pressure, 1, encoder.dir, 0, 200));
            }
            else {
              limit_maximum_pressure(clamp_input_value(limit.maximum.pressure, 1, encoder.dir, 50, 600));              
            }
            break;
          case MINUTE_VENTILATION_LIMIT:
            if(level == OTHER_VALUE_LEVEL) {
              limit_minimum_ventilation(clamp_input_value(limit.minimum.ventilation, 100, encoder.dir, 3000, 10000));
            }
            else {
              limit_maximum_ventilation(clamp_input_value(limit.maximum.ventilation, 100, encoder.dir, 3000, 10000));              
            }
            break;
          case TIDAL_VOLUME_LIMIT:
            if(level == OTHER_VALUE_LEVEL) {
              limit_minimum_volume(clamp_input_value(limit.minimum.volume, 5, encoder.dir, 180, ctrl.fullPressVolume));
            }
            else {
              limit_maximum_volume(clamp_input_value(limit.maximum.volume, 5, encoder.dir, 180, ctrl.fullPressVolume));              
            }
            break;

          /* SYSTEM_PAGE */
          case AUDIBLE_ALARM:
            break;
          case START_POSITION:
            ctrl_start_position(clamp_input_value(ctrl.startPosition, 50, encoder.dir, 500, 2000));
            if(phase == NO_PHASE) {
              move_to_position(ctrl.startPosition, live.expiratoryRpm, true);
            }
            break;
          case FULL_PRESS_VOLUME:
            ctrl_full_press_volume(clamp_input_value(ctrl.fullPressVolume, 10, encoder.dir, 400, 1000));
            break;
          case FACTORY_RESET:
            break;
          case RESTART:
            break;
        }
        break;

      case MENU_LEVEL: // encoder changes menu selection
        switch(page) {
          case HOME_PAGE:
            level = VALUE_LEVEL;
            break;
          case SELECT_PAGE:
            menu = clamp_input_value(menu, 1, encoder.dir, SELECT_MENU_MIN, SELECT_MENU_MAX);
            break;
          case CONTROLS_PAGE:
            selection = (selection_t)clamp_input_value(selection, 1, encoder.dir, CONTROLS_SELECTION_MIN, CONTROLS_SELECTION_MAX);
            break;
          case SETUP_PAGE:
            selection = (selection_t)clamp_input_value(selection, 1, encoder.dir, SETUP_SELECTION_MIN, ctrl.ventilationActive ? SETUP_SELECTION_MIN : SETUP_SELECTION_MAX);
            break;
          case LIMITS_PAGE:
            selection = (selection_t)clamp_input_value(selection, 1, encoder.dir, LIMITS_SELECTION_MIN, LIMITS_SELECTION_MAX);
            break;
          case EVENTS_PAGE:
            break;
          case SYSTEM_PAGE:
            selection = (selection_t)clamp_input_value(selection, 1, encoder.dir, SYSTEM_SELECTION_MIN, SYSTEM_SELECTION_MAX);
            break;
        }
    }
    encoder.dir = 0; // clear encoder pulse
    redraw = true;
  }
  
  /* ROTARY BUTTON BEHAVIOR
   * If home page, increment selection
   * If select page, select page
   * Else select value
   */
  
  rotaryButton.update(fastDigitalRead(ROTARY_BUTTON_PIN) ? 0 : 1);
  if(rotaryButton.pressed()) {
     //IF_DEBUG( debug.println("rotary button"); )
    switch(page) {
      case HOME_PAGE: // rotary button changes home page selection
        selection = (selection_t)(selection + 1);
        if(selection > HOME_SELECTION_MAX) {
          selection = HOME_SELECTION_MIN;
        }
        break;
      case SELECT_PAGE: // rotary button selects page
        page = (page_t)menu;
        switch(page) {
          case CONTROLS_PAGE:
            selection = CONTROLS_SELECTION_MIN;
            break;
          case SETUP_PAGE:
            selection = SETUP_SELECTION_MIN;
            break;
          case LIMITS_PAGE:
            selection = LIMITS_SELECTION_MIN;
            break;
          case SYSTEM_PAGE:
            selection = SYSTEM_SELECTION_MIN;
            break;
          default:
            break;
        }
        break;
      case LIMITS_PAGE: // rotary button toggles minimum and maximum limits
        switch(level) {
          case OTHER_VALUE_LEVEL:
            level = VALUE_LEVEL;
            break;
          case VALUE_LEVEL:
            level = MENU_LEVEL;
            break;
          case MENU_LEVEL:
            level = OTHER_VALUE_LEVEL;
            break;
        }
        break;
      case SETUP_PAGE:
        if(selection == START_STOP_VENTILATION) {
          ctrl.ventilationActive = !ctrl.ventilationActive;
          select_home_page();
        }
        else if(!ctrl.ventilationActive && selection == PRESSURE_TEST) {
          live.rpmRamp = 0;
          live.peakPressure = 0;
          move_to_position(ctrl.startPosition + live.tidalSteps, live.inspiratoryRpm, false);
          while(!stp.done) {
            live.pressure = read_pressure();
            if(live.basePressure == 0) live.zeroPressure = live.basePressure = live.pressure;
            adjust_rpm();
            if(redrawTimer < now) {
              redrawTimer = now + 200; 
              update_pressure();
            }
            if(redraw) {
              draw_update();
            }
          }
          move_to_position(ctrl.startPosition, live.expiratoryRpm, false);
        }
        break;
      case EVENTS_PAGE:
        events.length = 0;
        select_home_page();
        break;
      case SYSTEM_PAGE:
        if(selection == AUDIBLE_ALARM) {
          live.audibleAlarm = !live.audibleAlarm;
          select_home_page();
          break;
        }
        else if(selection == FACTORY_RESET) {
          factory_reset();
          page = HOME_PAGE;
          level = VALUE_LEVEL;
          selection = HOME_SELECTION_MIN;
          break;
        }
        else if(selection == RESTART) {
          wdt_disable();
          wdt_enable(WDTO_15MS);
          while(1) {}
        }
        // fall through
      default: // rotary button toggles between menu item and control value
        switch(level) {
          default:
            level = MENU_LEVEL;
            break;
          case MENU_LEVEL:
            level = VALUE_LEVEL;
            break;
        }
        break;
    }
    redraw = true;
  }

  /* STOP BUTTON BEHAVIOR
   * If alarm, disable alarm
   * If homing, emergency stop
   * Else, toggle home and select pages
   */

  stopButton.update(fastDigitalRead(STOP_BUTTON_PIN) ? 0 : 1); 
  if(stopButton.pressed()) {
     //IF_DEBUG( debug.println("stop button"); )
    if(alarm) { // stop button disables alarm
      alarm = NO_ALARM;
      page = EVENTS_PAGE;
      menu = SELECT_MENU_MIN;
    }
    else if(phase < NO_PHASE) {
      emergency_stop();
      phase = NO_PHASE;
    }
    else {
      switch(page) {
        case SELECT_PAGE:
          select_home_page();
          break;
        case HOME_PAGE:
          menu = SELECT_MENU_MIN;
          // fall through
        default: // stop button returns to previous menu
          page = SELECT_PAGE;
          level = MENU_LEVEL;
          break;
      }
    }
    redraw = true;
  }
  
  /* ENDSTOP BEHAVIOR
   * If homing, stop steppers and change phase to NO_PHASE
   * Else, stop steppers
   */

  homeEndstop.update(fastDigitalRead(HOME_ENDSTOP_PIN) ? 0 : 1); 
  if(homeEndstop.pressed()) {
     //IF_DEBUG( debug.println("home endstop"); )
    switch(phase) {
      case HOME_PHASE:
        move_to_position(ctrl.startPosition, live.expiratoryRpm, true);
        blue_led();
        break;
      case ENDSTOP_PHASE:
        phase = ZERO_PHASE;
        green_led();
        break;
      case ZERO_PHASE:
      default:
        break;
    }
    home_stop();
    move_to_position(ctrl.startPosition, live.expiratoryRpm, true);
    redraw = true;
  }

  live.pressure = read_pressure();
  if(redrawTimer < now) {
    redrawTimer = now + 200;
    update_pressure();
    redraw = true;
  }

  /* RESPIRATION CYCLE
   * Cycle the stepper motor movement through the phases to support mechanical breath
   */

  switch(phase) {
    case HOME_PHASE:
       //IF_DEBUG( debug.println("Homing"); )
      move_to_position(-((int)END_POSITION), live.expiratoryRpm, false); // home stepper motor until endstop
      phase = ENDSTOP_PHASE;
      redraw = true;
      break;
 
    case ENDSTOP_PHASE:
      if(stp.done) {
        phase = NO_PHASE;
        redraw = true;
      }
      break;
 
    case ZERO_PHASE:
      if(stp.done) {
        phase = NO_PHASE;
        redraw = true;
      }
      break;
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

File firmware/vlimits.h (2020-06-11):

#pragma once

/* PRESSURE LIMITS (ml H2O)
 * * * * * * * * * * * * * * * * */
#define MINIMUM_PRESSURE 0
#define DEFAULT_MINIMUM_PRESSURE 50
#define MAXIMUM_MINIMUM_PRESSURE 200
#define MINIMUM_MAXIMUM_PRESSURE 50
#define DEFAULT_MAXIMUM_PRESSURE 400
#define MAXIMUM_PRESSURE 600

#define PLATEAU_AIRWAY_PRESSURE_INCREMENT 10
#define DEFAULT_PLATEAU_AIRWAY_PRESSURE 300

/* MINUTE VENTILATION LIMITS (ml/min)
 * * * * * * * * * * * * * * * * */
#define MINIMUM_MINUTE_VENTILATION 1000
#define DEFAULT_MINIMUM_MINUTE_VENTILATION 5000
#define MAXIMUM_MINIMUM_MINUTE_VENTILATION 6000
#define MINIMUM_MAXIMUM_MINUTE_VENTILATION 3000
#define DEFAULT_MAXIMUM_MINUTE_VENTILATION 10000 
#define MAXIMUM_MINUTE_VENTILATION 30000
#define MINUTE_VENTILATION_INCREMENT 100

/* VOLUME LIMITS (ml)
 * * * * * * * * * * * * * * * * */
#define MINIMUM_VOLUME 150
#define DEFAULT_MINIMUM_VOLUME 180
#define MINIMUM_MAXIMUM_VOLUME 200
#define DEFAULT_MAXIMUM_VOLUME 750
#define VOLUME_INCREMENT 5

#define DEFAULT_TIDAL_VOLUME 450

/* RESPIRATORY RATE (bpm)
 * * * * * * * * * * * * * * * * */
#define MINIMUM_RESPIRATORY_RATE 10
#define DEFAULT_RESPIRATORY_RATE 12
#define MAXIMUM_RESPIRATORY_RATE 20

/* RESPIRATORY RATIO (1:x)
 * * * * * * * * * * * * * * * * */
#define MINIMUM_RESPIRATORY_RATIO 1
#define DEFAULT_RESPIRATORY_RATIO 3
#define MAXIMUM_RESPIRATORY_RATIO 5

/* TRIGGER PRESSURE (ml H2O)
 * * * * * * * * * * * * * * * * */
#define MINIMUM_TRIGGER_PRESSURE 0
#define DEFAULT_TRIGGER_PRESSURE 15
#define MAXIMUM_TRIGGER_PRESSURE 50

/* INSPIRATORY FLOW (l/min)
 * * * * * * * * * * * * * * * * */
#define MINIMUM_INSPIRATORY_FLOW 10
#define DEFAULT_INSPIRATORY_FLOW 35
#define MAXIMUM_INSPIRATORY_FLOW 60

/* EXPIRATORY FLOW (l/min)
 * * * * * * * * * * * * * * * * */
#define MINIMUM_EXPIRATORY_FLOW 10
#define DEFAULT_EXPIRATORY_FLOW 35
#define MAXIMUM_EXPIRATORY_FLOW 60

/* START POSITION (steps)
 * * * * * * * * * * * * * * * * */
#define MINIMUM_START_POSITION 500
#define DEFAULT_START_POSITION 1000
#define MAXIMUM_START_POSITION 5000
#define START_POSITION_INCREMENT 100

/* FULL_PRESS_VOLUME
 * * * * * * * * * * * * * * * * */
#define MINIMUM_FULL_PRESS_VOLUME 450
#define DEFAULT_FULL_PRESS_VOLUME 450
#define MAXIMUM_FULL_PRESS_VOLUME 850
#define FULL_PRESS_VOLUME_INCREMENT 10
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

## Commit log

2020-05-04 Files and images
    [Mask Manifold v5.f3d, Planetary Gear Module v9.f3z, base.stl, bearing_pin.stl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]
2020-05-04 Updated documentation
    Additional images and amended bill of materials.
2020-05-05 Added pcb files
    [BOM_Shield_PCB-v1.csv, PickAndPlace_Shield_PCB-v1.csv]
2020-05-05 Added stepper configuration
    [Mask Manifold v5.iges, Mask Manifold v5.step]
2020-05-05 Added 12v bypass
    [BOM_Shield_PCB-v1.csv, PickAndPlace_Shield_PCB-v1.csv]
2020-05-08 Fixed homing overrun
    Altered geometry of tie rod and panaetary output to prevent homing overun if switch fails. Added limits header. Changed step IO timing. General refactoring.
    [Planetary Gear Module v11.f3z, Planetary Gear Module v9.f3z, planet_output.stl, tie_rod.stl]
2020-06-11 Calibration Notes
2022-10-05 Added calibration data table for reference
